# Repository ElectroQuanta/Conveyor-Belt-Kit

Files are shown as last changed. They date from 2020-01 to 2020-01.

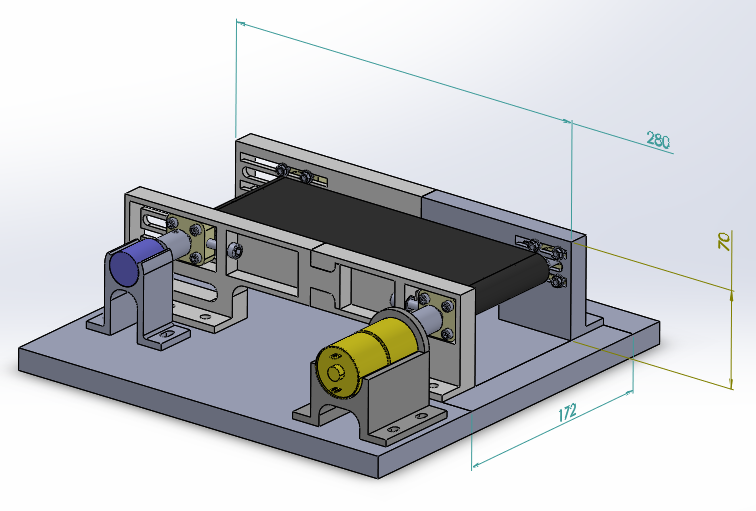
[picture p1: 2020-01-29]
Mechanics/mechanics.png

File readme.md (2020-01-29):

- [Introduction](#org74c4463)
  - [Motivation & Goals](#org79d08ed)
  - [Product concept](#orgb032d50)
- [Repository Struct](#org79cf582)

# Introduction

The present work, within the scope of the curricular unit of Laboratórios e Práticas Integradas I, consists in the project of the development of a product, namely, a pedagogic kit about automatic control. The theme selected by the project’s team was a conveyor belt, showcasing the velocity control of the load transported by the conveyor, independently from its mass. In this section are presented the project’s motivation and goals, the product concept, the project planning and the document organisation.

## Motivation & Goals

The main goal of the project is to develop a didactic kit to ease the learning of automatic control with the following characteristics:

-   Low complexity — to be an useful tool in a wide range of ages;
-   Subject comprehensive — to be able to integrate topics on several domains of electronics engineering, with particular focus on the curricular units taught on the fifth semester of the MIEEIC;
-   affordable: to allow replication and usage by any social stratum;
-   safe: without posing any danger for the user well-being and the surrounding ones, as well as not causing any materials.
-   didactic: fostering the learning on the topics in a practical and fun way;
-   pedagogic: documenting the project to allow replication by any individual in a simple and convenient manner.

## Product concept

The envisioned product consists of a didactic kit to enable the learning about automatic control. For this purpose, it focuses on a simple control problem — load movement control (velocity and direction) in a conveyor, similar to the ones present at the airports for user transportation. However, it will allow the user to experiment several types of controllers and the effect of each one in the system to control.

The goal is to control the velocity of the conveyor, virtually independently of its load. Thus, the addition or removal of load (e.g. passengers) should not affect the velocity of the conveyor. Additionally, the transportation direction must also be modifiable.

Furthermore, a laboratory guide is to be produced, similar to the ones used in Laboratórios e Práticas Integradas I (LPI1).

# Repository Struct

-   Control Guidebook: contains the guidebook created from the project
-   Datasheets: contains the relevant electronics datasheets
-   Manuals: contains the assembly manual and the user manual
-   Mechanics: contains the mechanics parts (STL format) for 3D printing:
-   PCB: printed circuit board - Bill of Materials, Schematics and Layouts
-   Simulations: control simulations
-   Tests: relevant tests performed

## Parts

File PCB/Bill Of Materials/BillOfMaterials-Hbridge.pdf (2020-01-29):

|Bill Of Materials for h-bridge_circuit.sch on Mon Jan 20 15:50:08 2020 | |
|Item|Qty |Reference|Part Name | |Manufacturer | |Description | |Value |
|----+----+---------+--------------+--------------+-----------------------------+------|
|1 | |1 | |C2 | |CAP-CK05,10n, |KEMET | |RADIAL CERAMIC CAPACITOR, | |10n | |
| | | | | | |??? | | | |MIL-SPEC SIZE CK05 | | | |
|2 | |1 | |C1 | |CAP-CK05,22n, |KEMET | |RADIAL CERAMIC CAPACITOR, | |22n | |
| | | | | | |??? | | | |MIL-SPEC SIZE CK05 | | | |
|3 | |1 | |C4 | |CAP-CX12-B,1u,|KEMET | |POL. DIPPED SOLID TANT. CAP. |1u | |
| | | | | | |??? | | | |MIL-SPEC SIZE CX12 CASE 'B' | | | |
|4 | |1 | |C3 | |CAP-CX12-B, | |KEMET | |POL. DIPPED SOLID TANT. CAP. |22u | |
| | | | | | |22u,??? | | | |MIL-SPEC SIZE CX12 CASE 'B' | | | |
|5 | |2 | |J1 J4 | |CONRA-2P-200 | | | |RIGHT ANGLE 2-PIN M/F | | | |
| | | | | | | | | | |HORIZONTAL PCB CONNECTOR | | | |
|6 | |1 | |J3 | |CONRA-3P-200 | | | |RIGHT ANGLE 3-PIN M/F | | | |
| | | | | | | | | | |HORIZONTAL PCB CONNECTOR | | | |
|7 | |4 | |D1-4 | |DIODE | | | |GENERIC DIODE W ALTERNATE | | | |
|8 | |1 | |F2 | |FUSE | | | | | | | |
|9 | |1 | |U1 | |L298N | | | |Dual_Full_Bridge_Motor_Driver| | |
| | | | | | | | | | |_15-Pin(15+Tab)_MULTIWATT_V_T| | |
| | | | | | | | | | |ube | | | |
|10 | |1 | |U2 | |MC7805ACT | |MOTOROLA | |POSITIVE VOLTAGE REGULATOR; | | | |
| | | | | | | | | | |FIXED +5.0 VOLTS | | | |
|11 | |4 | |H1-4 | |PCB_HOLE | | | | | | | |

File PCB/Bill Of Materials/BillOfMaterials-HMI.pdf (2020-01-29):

|Bill Of Materials for hmi_circuit.sch on Mon Jan 20 15:45:06 2020 | |
|Item|Qty |Reference|Part Name | |Manufacturer | |Description | |Value |
|----+----+---------+--------------+--------------+-----------------------------+------|
|1 | |1 | |C2 | |CAP-CK05,10n, |KEMET | |RADIAL CERAMIC CAPACITOR, | |10n | |
| | | | | | |??? | | | |MIL-SPEC SIZE CK05 | | | |
|2 | |1 | |C1 | |CAP-CK05,22n, |KEMET | |RADIAL CERAMIC CAPACITOR, | |22n | |
| | | | | | |??? | | | |MIL-SPEC SIZE CK05 | | | |
|3 | |1 | |J1 | |CONRA-2P-200 | | | |RIGHT ANGLE 2-PIN M/F | | | |
| | | | | | | | | | |HORIZONTAL PCB CONNECTOR | | | |
|4 | |1 | |J2 | |CONRA-4P-200 | | | |RIGHT ANGLE 4-PIN M/F | | | |
| | | | | | | | | | |HORIZONTAL PCB CONNECTOR | | | |
|5 | |1 | |LED_DRIVE|LM3914N | | | |<b>LED_DRIVER</b><p>_senses_a| | |
| | | | |R | | | | | |nalog_voltage_levels_and_driv| | |
| | | | | | | | | | |es_10_LEDs | | | |
|6 | |1 | |VREG | |MC7805ACT | |MOTOROLA | |POSITIVE VOLTAGE REGULATOR; | | | |
| | | | | | | | | | |FIXED +5.0 VOLTS | | | |
|7 | |10 | |L1-10 | |MLED71 | |MOTOROLA | |INFRARED LED | | | |
|8 | |4 | |HOLE1-4 | |PCB_HOLE | | | | | | | |
|9 | |3 | |R1 R3-4 | |RES-1/8W,10k | | | |RES BODY:060 CENTERS:400 | |10k | |
|10 | |1 | |R2 | |RES-1/8W,2.2k | | |RES BODY:060 CENTERS:400 | |2.2k | |
|11 | |1 | |SW2 | |SWITCH-SP,??? | | |SWITCH | |??? | |
|12 | |1 | |SW1 | |SWITCH-ST | | | |WIRE CONNECTION | | | |
|13 | |1 | |POTV | |VRES-TOP-ADJ | | | |VARIABLE RESISTOR (TOP ADJUST| | |
| | | | | | | | | | |TYPE) | | | |

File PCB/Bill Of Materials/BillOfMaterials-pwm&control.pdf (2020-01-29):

|Bill Of Materials for Pwm_Control_V4.sch on Fri Jan 24 15:55:29 2020 | |
|Item|Qty |Reference|Part Name | |Manufacturer | |Description | |Value |
|----+----+---------+--------------+--------------+-----------------------------+------|
|1 | |1 | |C3 | |CAP-CK05,10n, |KEMET | |RADIAL CERAMIC CAPACITOR, | |10n | |
| | | | | | |??? | | | |MIL-SPEC SIZE CK05 | | | |
|2 | |1 | |C2 | |CAP-CK05,22n, |KEMET | |RADIAL CERAMIC CAPACITOR, | |22n | |
| | | | | | |??? | | | |MIL-SPEC SIZE CK05 | | | |
|3 | |1 | |C1 | |CAP-CK05,330n,|KEMET | |RADIAL CERAMIC CAPACITOR, | |330n | |
| | | | | | |??? | | | |MIL-SPEC SIZE CK05 | | | |
|4 | |1 | |C5 | |CAP-CK05,???, |KEMET | |RADIAL CERAMIC CAPACITOR, | |??? | |
| | | | | | |??? | | | |MIL-SPEC SIZE CK05 | | | |
|5 | |1 | |C4 | |CAP-CX12-B, | |KEMET | |POL. DIPPED SOLID TANT. CAP. |??? | |
| | | | | | |???,1u | | | |MIL-SPEC SIZE CX12 CASE 'B' | | | |
|6 | |1 | |J2 | |CONRA-2P-200 | | | |RIGHT ANGLE 2-PIN M/F | | | |
| | | | | | | | | | |HORIZONTAL PCB CONNECTOR | | | |
|7 | |1 | |J1 | |CONRA-5P-200 | | | |RIGHT ANGLE 5-PIN M/F | | | |
| | | | | | | | | | |HORIZONTAL PCB CONNECTOR | | | |
|8 | |2 | |D1-2 | |DIODE | | | |GENERIC DIODE W ALTERNATE | | | |
|9 | |1 | |U1 | |LM324 | |MOTOROLA | |QUAD DIFFERENTIAL INPUT | | | |
| | | | | | | | | | |OPERATIONAL AMPLIFIER | | | |
|10 | |1 | |U2 | |MC7805ACT | |MOTOROLA | |POSITIVE VOLTAGE REGULATOR; | | | |
| | | | | | | | | | |FIXED +5.0 VOLTS | | | |
|11 | |1 | |D6 | |MLED71 | |MOTOROLA | |INFRARED LED | | | | |
|12 | |4 | |H1-4 | |PCB_HOLE | | | | | | | | |
|13 | |2 | |R1 R6 | |RES-1/4W,100k | | |RES BODY:100 | CENTERS:500 | |100k | |
|14 | |2 | |R2 R22 | |RES-1/4W,10k | | | |RES BODY:100 | CENTERS:500 | |10k | |
|15 | |1 | |R7 | |RES-1/4W,1k | | | |RES BODY:100 | CENTERS:500 | |1k | |
|16 | |1 | |R5 | |RES-1/4W,200 | | | |RES BODY:100 | CENTERS:500 | |200 | |
|17 | |1 | |R3 | |RES-1/4W,43k | | | |RES BODY:100 | CENTERS:500 | |43k | |
|18 | |1 | |R8 | |RES-1/4W,51k | | | |RES BODY:100 | CENTERS:500 | |51k | |
|19 | |15 | |R9-21 | |RES-1/4W,??? | | | |RES BODY:100 | CENTERS:500 | |??? | |
| | | | |R23-24 | | | | | | | | | | |
|20 | |2 | |U3-4 | |TL084CN | | | |JFET_quad_operational_amplifi| | |
| | | | | | | | | | |ers | | | | |
|21 | |1 | |R4 | |VRES-TOP-ADJ | | | |VARIABLE RESISTOR (TOP ADJUST| | |
| | | | | | | | | | |TYPE) | | | | |

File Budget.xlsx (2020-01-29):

Description | Value (€) | Supplier | Category
Electronic box & Connectors | 15.98 | Leroy Merlin | Casing & Connectors
Electronic box connectors & Power supply connectors | 4.4 | Botnroll | Casing & Connectors
Power supply case | 3.69 | Botnroll | Casing & Connectors
Mechanical Components | 14 | ELAX | Mechanical
Mechanical 3D printed components | 20 | NEEEICUM | Mechanics
Control PCB components | 4.92 | Botnroll | PCB
Actuator PCB | 6 | Oficinas DEI | PCB
Actuator PCB components | 10.55 | Botnroll | PCB
Control PCB | 11 | Oficinas DEI | PCB
HMI PCB | 6 | Oficinas DEI | PCB
Total | 96.54

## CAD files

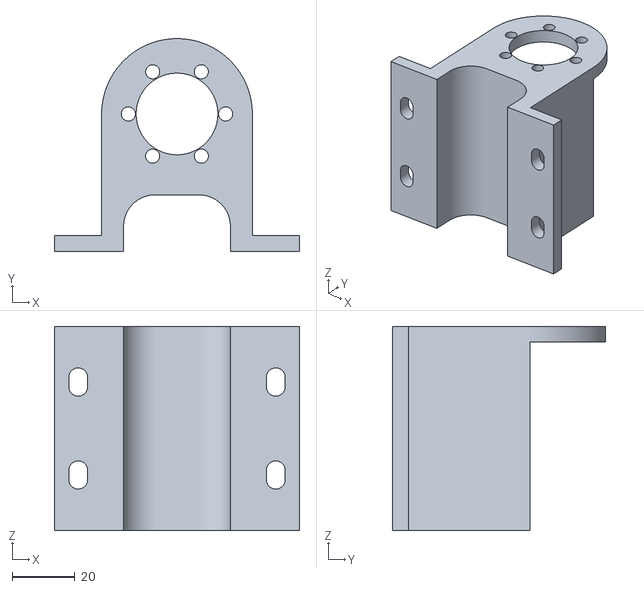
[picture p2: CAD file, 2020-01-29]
Mechanics/STL/Suporte_Motor.STL
78.0 x 67.8 x 65.0

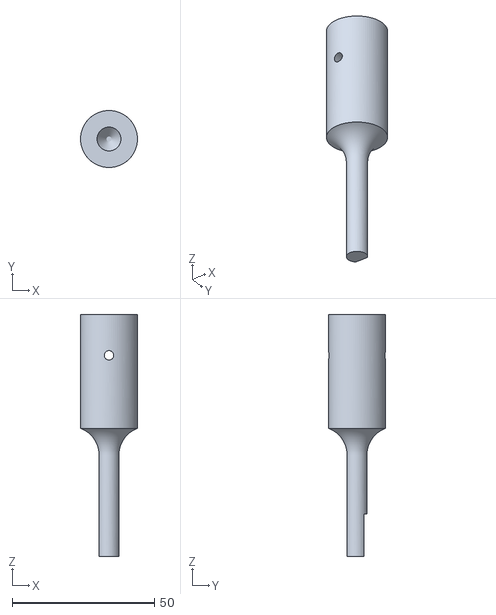
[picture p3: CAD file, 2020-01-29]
Mechanics/STL/Veio_2B_new_version.STL
20.0 x 20.0 x 85.0

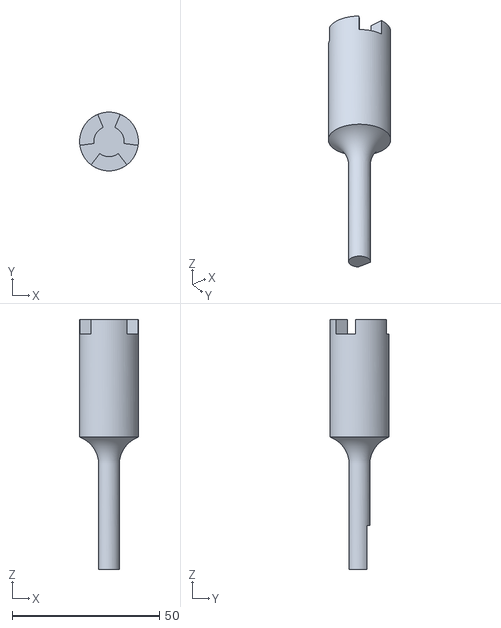
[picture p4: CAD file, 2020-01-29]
Mechanics/STL/Veio_1B.STL
20.0 x 20.0 x 85.0

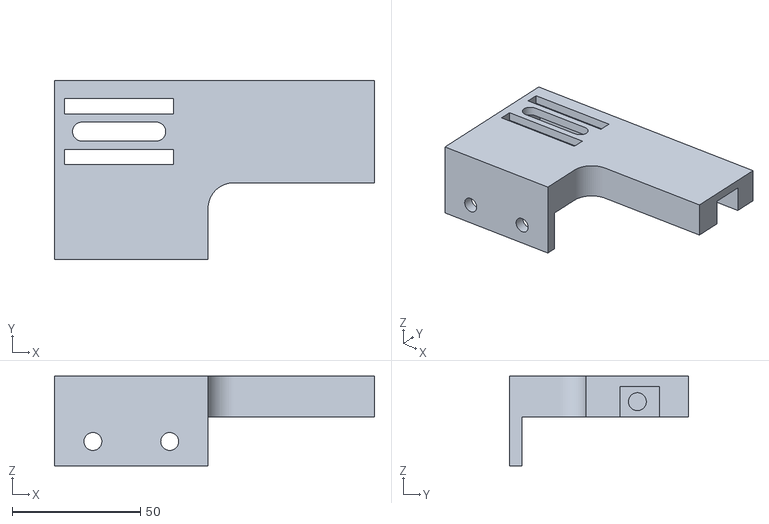
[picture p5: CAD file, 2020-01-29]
Mechanics/STL/Estrutura_1B.STL
125.0 x 70.0 x 35.0

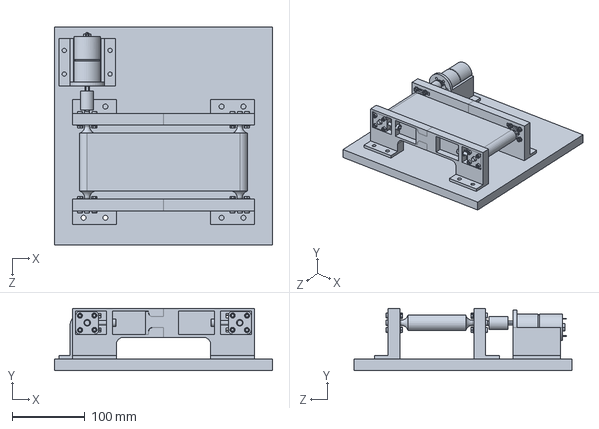
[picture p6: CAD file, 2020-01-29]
Mechanics/STL/Veio_1A_x2.SLDPRT
300.0 x 86.0 x 300.0 mm

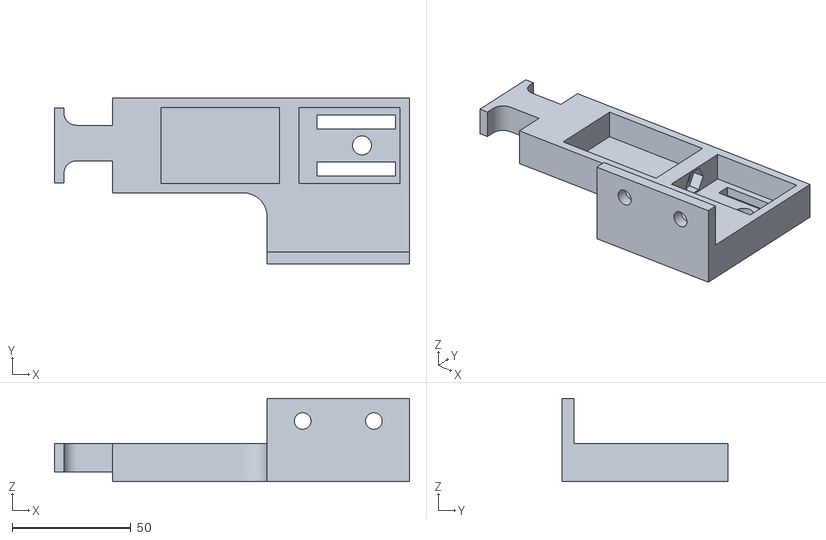
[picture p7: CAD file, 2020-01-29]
Mechanics/STL/Apoio_estutura_2.STL
149.5 x 70.0 x 35.0

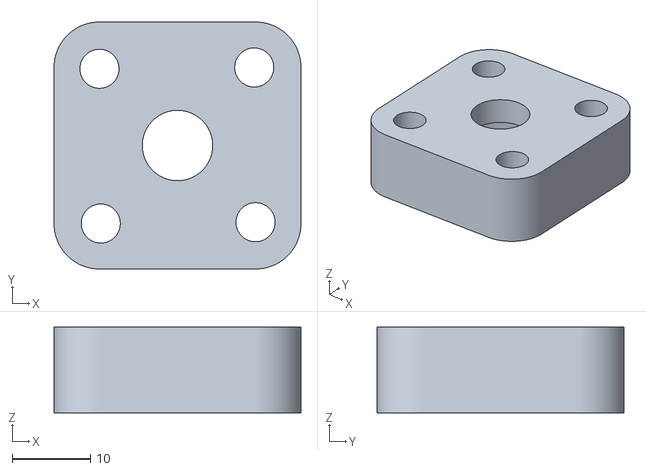
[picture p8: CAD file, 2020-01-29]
Mechanics/STL/Tensionador_x4.STL
31.6 x 31.6 x 11.0

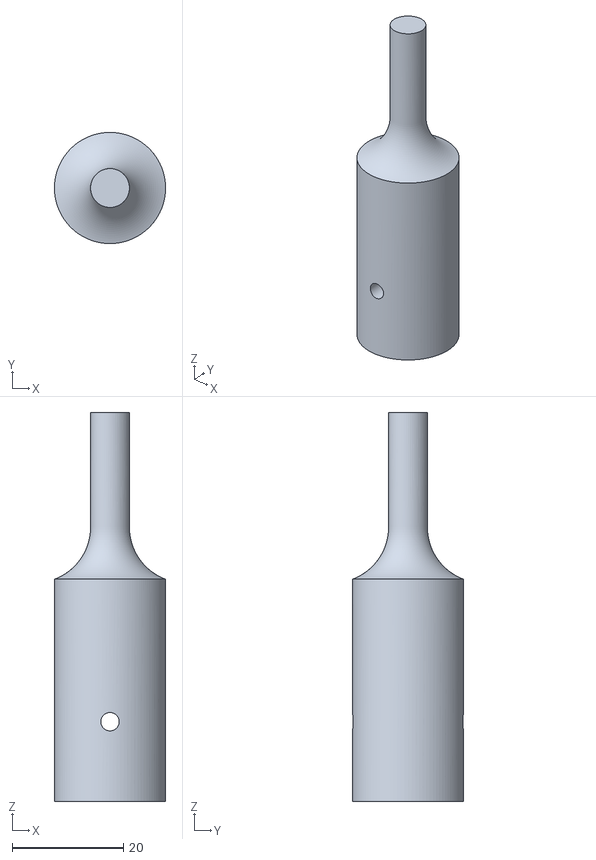
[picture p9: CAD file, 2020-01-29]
Mechanics/STL/Veio_2A_new_version.STL
20.0 x 20.0 x 70.0

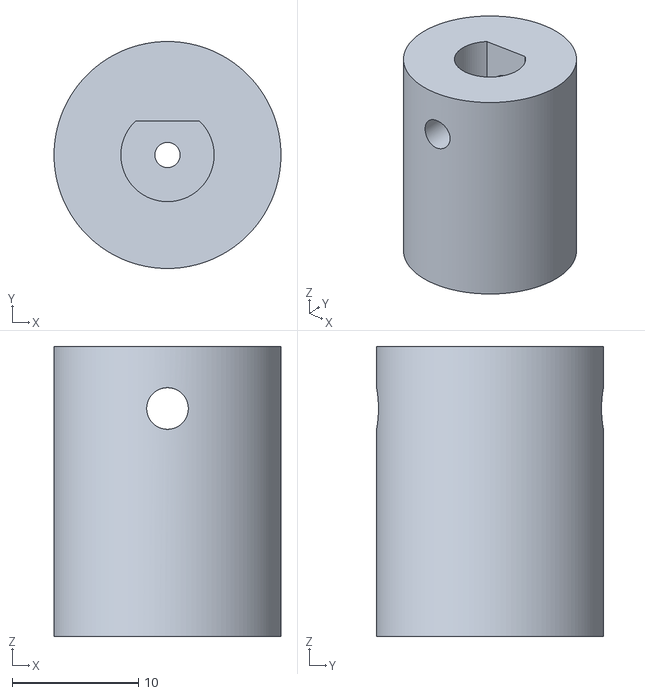
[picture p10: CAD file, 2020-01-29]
Mechanics/STL/Acoplamento_motor_feedBack.STL
18.0 x 18.0 x 23.0

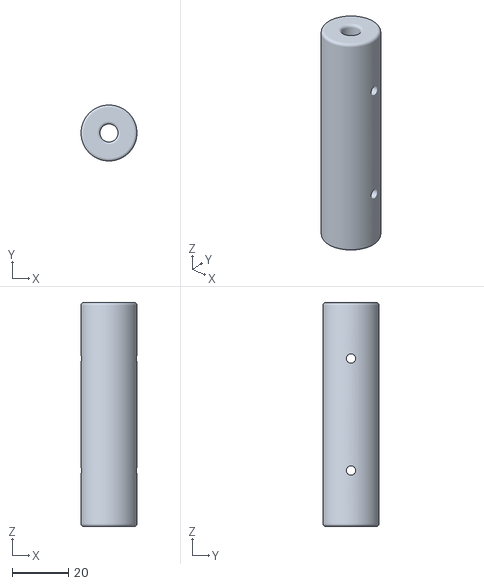
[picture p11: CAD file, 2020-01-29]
Mechanics/STL/Cilindro_veio_6mm.STL
20.0 x 20.0 x 80.0

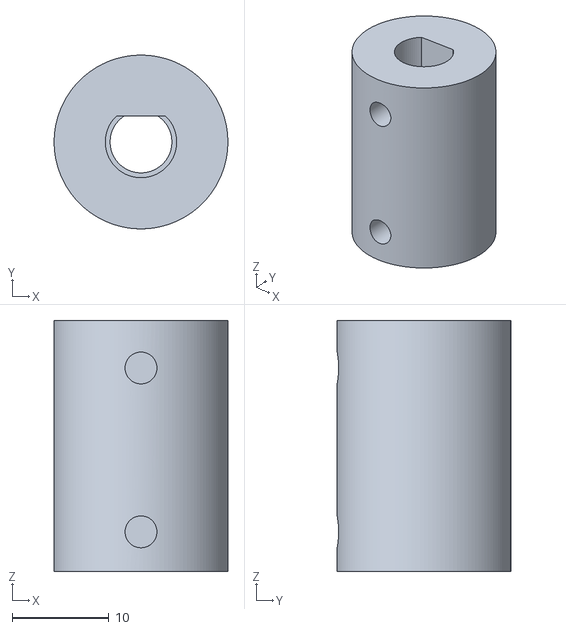
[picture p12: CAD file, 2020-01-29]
Mechanics/STL/Acoplamento.STL
18.0 x 18.0 x 26.0

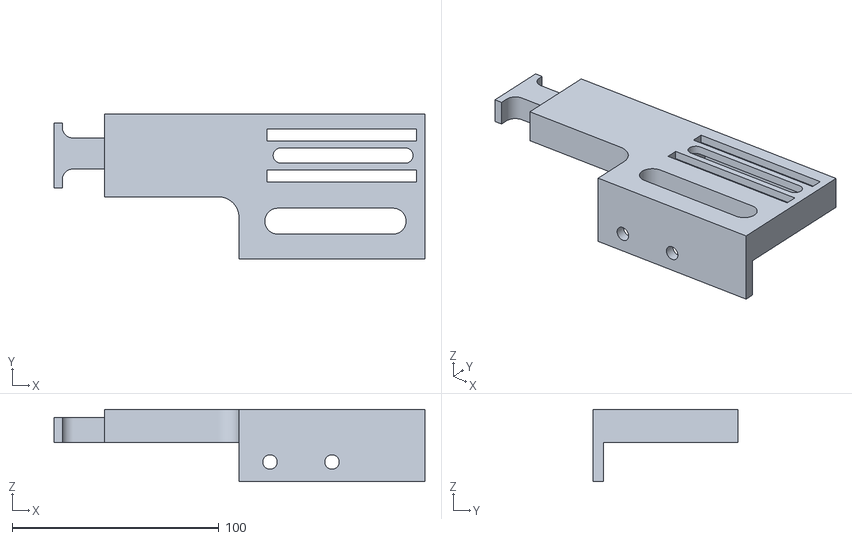
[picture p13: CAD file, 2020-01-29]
Mechanics/STL/Estrutura_2B.STL
179.5 x 70.0 x 35.0

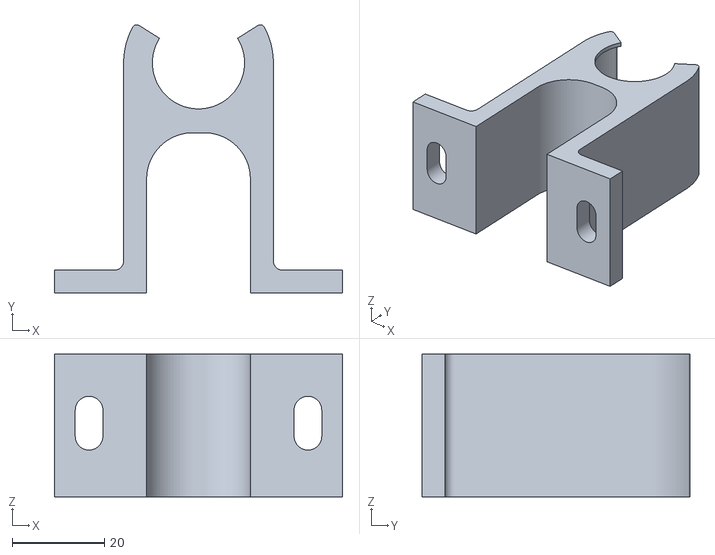
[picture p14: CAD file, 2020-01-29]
Mechanics/STL/Suporte_Motor_feedBack.STL
62.5 x 58.3 x 31.0

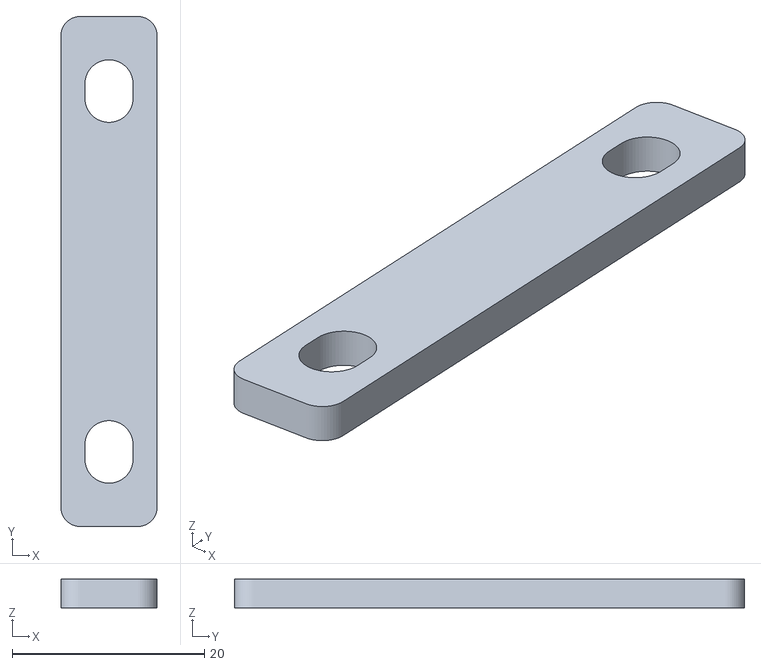
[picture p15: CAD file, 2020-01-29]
Mechanics/STL/Suporte_placa.STL
10.0 x 53.0 x 3.00

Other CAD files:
Mechanics/STL/Veio_2B.STL
Mechanics/STL/Apoio_estutura_1.STL
Mechanics/STL/Estrutura.STL
Mechanics/STL/Apoio_veio.STL
Mechanics/STL/Estrutura_1A.STL
Mechanics/STL/Estrutura_2A.STL
Mechanics/STL/Veio_1A_x2.STL
Mechanics/STL/Veio_1B_new_version.STL

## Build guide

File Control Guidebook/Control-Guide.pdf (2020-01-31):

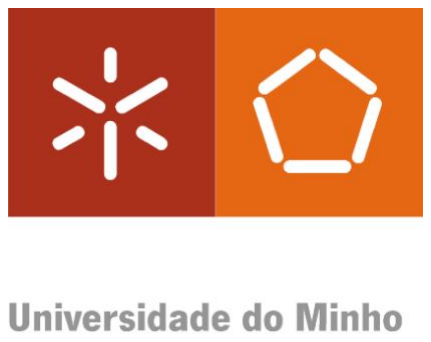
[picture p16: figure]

## Laboratório e Práticas Integradas I 2019/20 Integrator Project

## Integrated Master´s in Engineering

## Industrial Electronics and Computers

# Conveyor Belt velocity control: laboratory guide

Group 3:

José Pires | A50178
Hugo Carvalho | A85156
Nuno Rodrigues | A85207
João Faria | A85632
João Carvalho | A83564
Hugo Ferreira | A80665

30th January of 2020

## 1.Introduction

This laboratory practice focuses on the control of the velocity of a conveyor belt considering all types of control on the curriculum of the UC Automatic Control + Proportional-Integral.

Specifically, an electronic system will control a laboratorial model of a conveyor belt, which allows the simulation of all characteristics of the merchandised version, represented Figure 1.

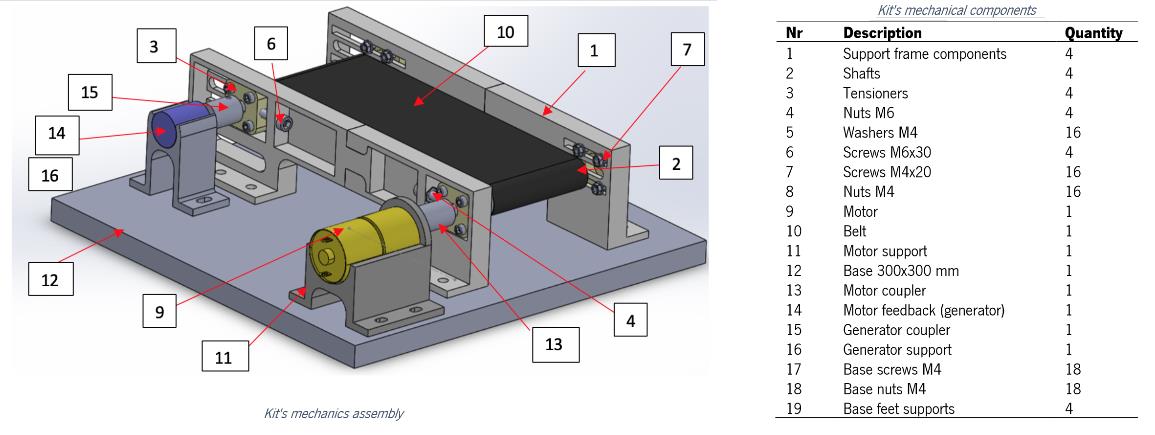
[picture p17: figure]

Figure 1- Laboratorial Model of Conveyor Belt

The motor is fed a voltage causing it to start rotating. The generator, acting as a sensor, will then apply a voltage to its terminals, based on the conveyor belt’s speed, thus providing a feedback path for the control.

The control system will require a sensor, a controller and an actuator.
As mentioned before, in this model of the conveyor belt, the generator will act as the sensor, supplying a “variable to control”.

The controller has several duties:

- Establishing a reference variable, or more accurately, an electrical representation of it.
- Establishing the electrical representation of the error.
- Establishing a command voltage, using the reference and measured variables previously

mentioned and a control rule.

In this model, there will be several controllers, each employing a different control rule, present in this document on Figure 3 and Figure 6.

The actuator serves as the connector between motor and controller, it will apply the command variable on the motor, permitting that the controller’s changes to the system be shown.

The control rules to be applied can be succinctly described as follows:

- On-Off Control – It applies the maximum value of the command variable or the minimum

(in this case 0). In this specific case, the motor will either be rotating at full speed or not

rotating at all.

- Proportional Control – It applies a command variable between its maximum and minimum

value, proportional to the error.

- Proportional-Integral Control – Serves the same purpose as proportional control, control-

wise, but allows for better system performance, specifically by reducing the steady-state’s

error.

Due to the motor’s characteristics the actuator needs to be an H-bridge, represented by Figure 5.

All control rules require simulation, to implement a control rule without a clear idea of its consequences to the system, can be disastrous both for the model as well for a future career in engineering. In order to simulate, the system’s mathematical model and physical constant values must be obtained.

In all that follows consider +Vcc=12V and -Vcc=-12V. The opamps to be used are LM304 or equivalents.

## 2. Mathematical model

This prototype uses a DC motor and a reduction box with a reduction ratio of G:1 to move a cylinder that will in turn move the conveyor. Another DC motor, working as a generator is at the end of the conveyor, the latter moves a cylinder that will in turn move the generator.

Definitions:

J1: Motorized Cylinder’s Moment of Inertia

J2: Generator Cylinder’s Moment of Inertia

M: Conveyor’s Mass

w: Cylinder’s Angular Velocity

B: System’s Supposedly Linear Coefficient of Friction

The conveyor’s velocity (Control Variable) will be obtained by v = w * r, r being the cylinder’s radius. With this equality in mind we can obtain the system’s Lagrangian function:

L =

1
2

(J1 + J2 + Mr

2

)w²

With the Lagrangian, the system’s equation based on the torque is obtainable:

(J1 + J2 + Mr

2)

dw
dt = T − Bw (2)

Considering that the motor is of the DC variant and using the following definitions:

Ka: Motor’s Electromechanical Constant

I: Motor’s Current

Ua: Motor’s Voltage

R: Rotor’s Resistance

wm: Motor’s Angular Velocity

This relation is obtained:
T = G ∗ Ka ∗ I

I =

1
R

(Ua − Ka ∗ wm)

Considering that:

wm = G ∗ w

The expression above can be simplified further: T = Km ∗ I,Km = Ka ∗ G

I =

1
R

Ua −

Km
R

w

In conclusion, the following model is obtained:

(J1 + J2 + Mr

2
)

dw
dt + (B +

(Km)

2
R

)w =

Km
R

Ua

A first-degree model with one control variable resulting in a single feedback gain.

## 2.1 – Obtain the physical constants of the system

Before drafting any kind of control diagram, the system’s physical constants are required for an accurate simulation. Following the mathematical module, the following constants are required:

- M – Conveyor’s mass
- m – Cylinder’s mass
- r – Radius of the cylinder’s base
- J1 – Moment of inertia of the motor’s cylinder
- J2 – Moment of inertia of the generator’s cylinder
- B – Supposedly linear coefficient of friction
- Km – Motor’s electromechanical constant (with reduction box)
- R – Rotor’s resistance

2.1.1- Measure M, m and r with appropriate measuring instruments and calculate J1 and J2 with those values.

2.1.2 – Run a series of tests to obtain physical constants.

Consider the following equations:

Km =

T
I

B =

T
w

Un = R ∗ ia + Ka ∗ w
≡ R = Un/Ia + 0, w = 0

T − Torque obtained when the motor is rotating at a constant angular velocity. I – Nominal current.
w – The constant angular velocity of the motor.
Un – Nominal voltage of the motor.
Ia – Start-up current of the motor.

2.1.2.1- Build a simple circuit with a DC power source (+Vcc) in series with a 1-ohm resistor and the motor. Measure, with an amperemeter, the current that passes through the motor when it rotates with constant velocity. Calculate the motor’s potency.

2.1.2.2- With the motor’s potency, calculate the torque and with it Km and B.

2.1.2.3- With the same circuit as in 1.2.1, using an oscilloscope measure the motor’s startupcurrent and calculate R.

## 3 – On-Off Control Simulation

Before implementing any electronic circuit with the purpose of controlling a system, the method
of control | must | be | chosen | and | its | suitability | towards | the | system | analyzed.
Following the Automatic Control UC’s curriculum, on-off control will be considered first:

3.1- Using the provided mathematical module and system’s physical constants develop a simulation draft implementing on-off control.

3.2- Draw conclusions considering the physical consequences of the system’s behavior with on-off control. Can it be implemented? Should it be implemented? Justify your answers adequately.

## 4- Proportional Control Simulation

Once again before considering implementing a circuit, the control rule’s compatibility towards the system must be tested through simulation.

4.1- Develop a simulation draft using proportional control. Obtain an appropriate gain, that is physically possible to use for proportional control.

4.2- Draw conclusions. Does the system do what its supposed to? Does it reach the level of control desired? Why?

4.3- Compare to the results of the on-off simulation. Is it better? Why?

## 5-Measure the voltage of generator

As the belt moves, a voltage in the terminals of the generator appears in the mV range. This voltage is crucial to control the velocity of the belt, it is the feedback signal that informs the controller of the value of the velocity of the belt. This value will be compared to the reference voltage, which varies between 0 and 5V so the voltage of the generator needs to be betwixt 0 and 5 V as well.

To do so, the first thing is to make a motor and generator test, where one varies the voltage in the motor and reads the voltage in the terminals of the generator. Inputting the values in an excel sheet and drawing the tendency line, the result must be an almost linear slope. This slope defines the gain necessary to use in a non-inverting opamp montage.

Furthermore, the generator voltage must pass throw a low pass filter for the ripple oscillations to disappear.

After the non-inverting opamp montage, it must pass through a full-wave rectifier (R4=R5). Should the motor be rotating counter-clockwise, the voltage at the generator’s terminals will be negative, which must not happen for our actuator is an H-Bridge.

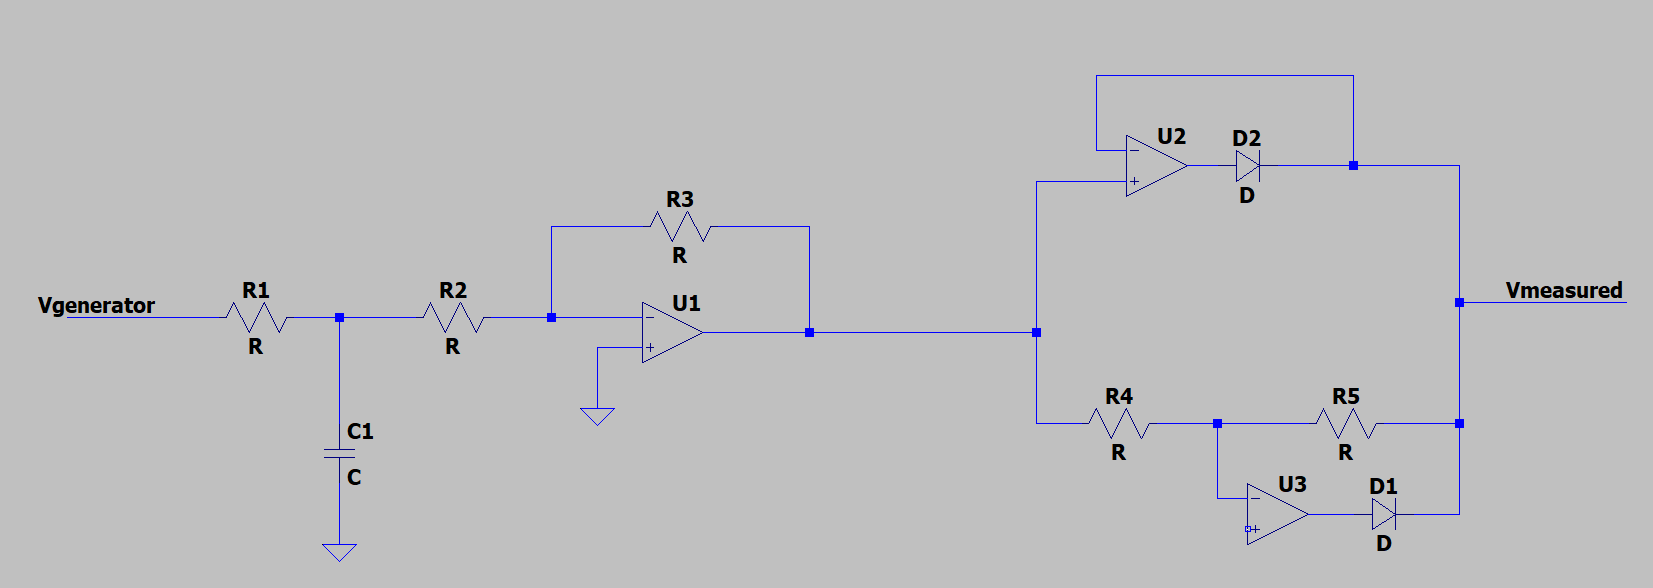
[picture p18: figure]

Figure 2 – Vmeasured Circuit

5.1 – Make the motor/generator test and draw the tendency line in excel.

5.2- Dimension R1 and C1 for the cutoff frequency to be 1 Hz.

5.3- Dimension R2 and R3 for Vmeasured to vary between 0 and 5V

## 6-Proportional Control Circuit

The implementation of proportional control can be obtained by the circuit in Figure 3.

The circuit using +Vstat, the RV1 potentiometer and 100-ohm resistor serves allows the generation of a Vreference voltage, the electrical representation of the conveyor’s desired velocity. The A2 opamp with the R3 and R4 resistors implement a subtractor resulting in:

Vcommand =

R3
R4

(Vreference − Vmeasured)

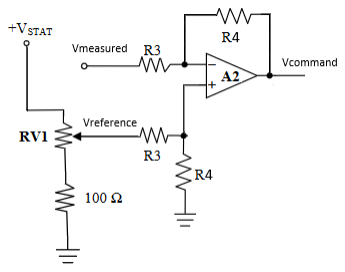
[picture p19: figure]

Figure 3- Circuit Implementing Proportional Control Rule

6.1-Study the behaviour of the circuit in Figure 3.

6.2- Calculate adequate values for R3 and R4 in order to obtain the gain that was deemed adequate in the simulation.

6.3- Assemble the circuit and test its behaviour. Make sure the opamp is behaving correctly.

## 6A-PWM based actuator

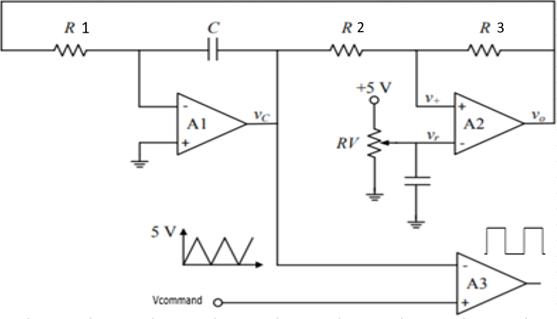
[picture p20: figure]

Figure 4- PWM signal generated by PWM modulator

Amplifier A1 is used in an inverter integrating assembly. Amplifier A2 is used in a non-inverting comparator assembly with hysteresis. Together, they generate a triangular wave between 0 and 5 V. The A3 amplifier performs a simple comparator, generating the PWM wave whose duty cycle is modified as the command tension varies.

The output wave, is high when the command voltage is higher than the triangular wave produced in the feedback loop, see Figure 4. Otherwise, it stays at 0V.

The PWM wave generated in the A3 interchanges between two values: 0V and 5V. However, when the duty cycle is changed (the time when it is 5V is changing) the medium voltage modifies, which is the product of the duty-cycle times high voltage (5V). That can be done, modifying the command voltage.

6.1A- Calculate the value of the components in the triangular wave:

a) Obtain the Vc expression in function of R1, C and Vo.
b) Determine R1 and C such that Vc takes 20ms from 0V to 5V.
c) Determine R2, R3 and Vr so that the comparator changes between 0V and 5V when Vo is +Vsat or -Vsat. Measure +Vsat and -Vsat.

6.2A- Draw Vo and Vc from 0ms to 40 ms.

6.3A- Draw Vcommand graph in function of Duty-cycle.

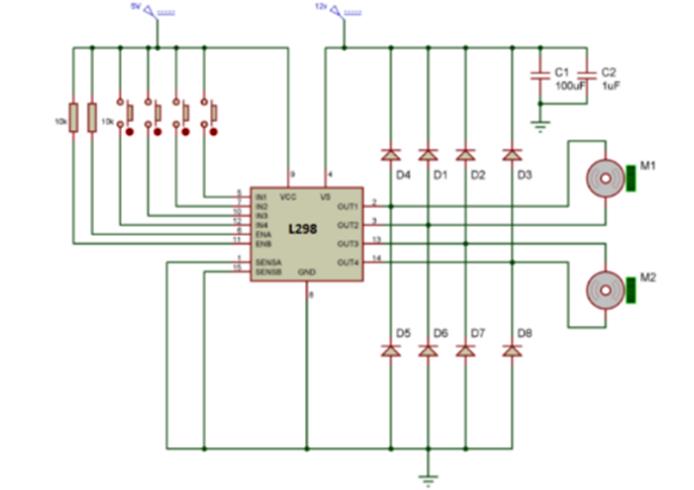
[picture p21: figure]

Figure 5- Actuator Circuit with the actuator part

6.4A- Which terminal should the A3 output be connected to? Assemble the following circuit, above in Erro! A origem da referência não foi encontrada.. Hint: The Enable terminal enables L298 internal H-Bridge.

a) Does the motor spin? Since only one motor will be used, which components are not useful for controlling motor M1?
b) Try pressing different buttons and adjust Vcommand so that the motor spins half the nominal value. Measure OUT1 and OUT2 tension.
c) Make the motor tension/velocity test and draw the tendency line in excel.

6.5A- Join the actuator’s exit to the motor’s terminals and observe the results. Does the system achieve the desired control?

## 7-PI Control

PI control is needed for non-integrating processes, in other words, any process that returns the same output given the same set of inputs and disturbances, one such example is a system whose control is not capable of reaching the desired level of control, normally due to physical limitations, more specifically once a certain point in the system’s response is reached, no matter how much the input or disturbance is changed (within physical reason of course) the system’s response will not change. In other words, a constant steady-state error is present!

The integrator will calculate the integer of the error and add it to Vcommand, therefore slowly reducing the steady-state error. The higher the integral gain, the faster the system’s steady-state error will decrease.

Vcommand = Kp ∗ Error + Ki ∗ ∫ Error

Integrator Output = −

1
R11 ∗ C

∫ Error

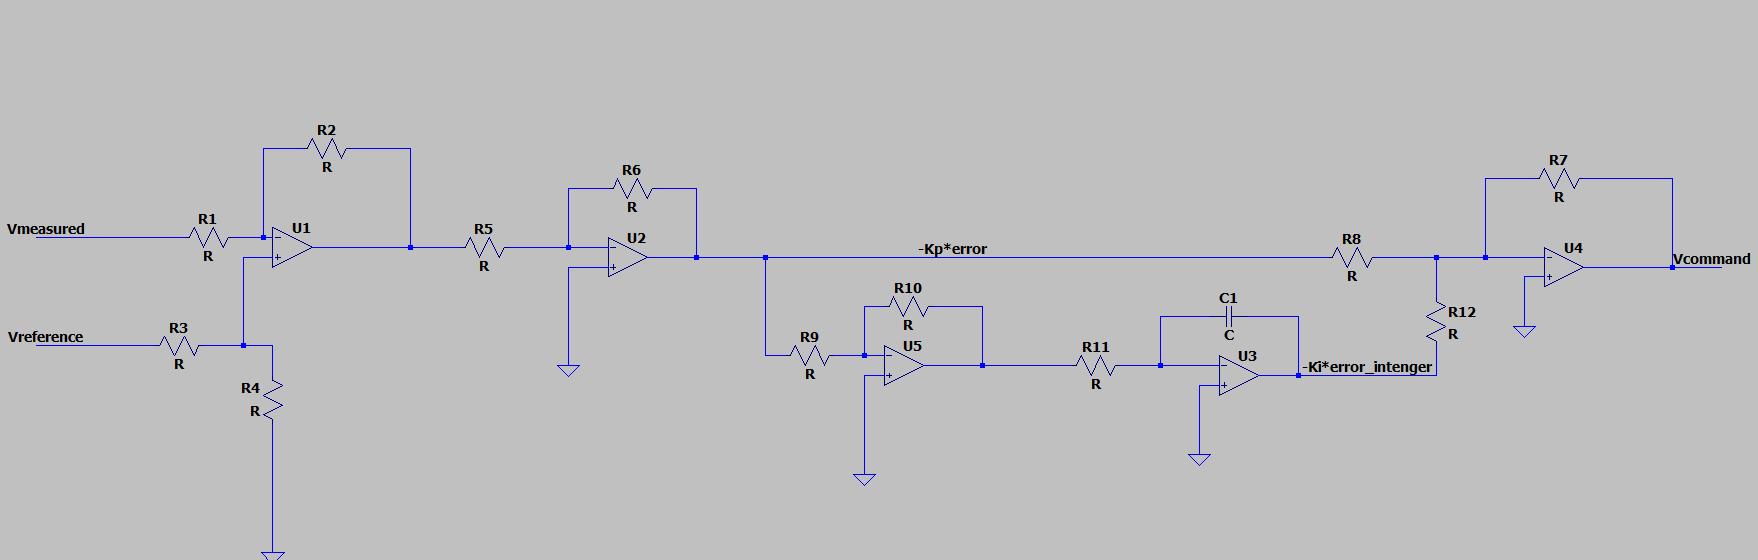
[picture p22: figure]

Figure 6- Circuit Implementing PI Control rule, R5=R6=R9=R10=R8=R7=R12=R7

7.1- Using the simulation diagram for 3.1, add integral control and comment on the result. Obtain a value for the integrator’s gain.

7.2- Study the circuit in Figure 6. What is the purpose of amplifiers U2, U3 and U5?

7.3- Use the PWM actuator to test the PI control on the motor. Measure the conveyor’s velocity and see if it reaches the value its supposed to. Compare to the results of the proportional gain.

7.4- Could PID control be used for this model? Why/Why not? What would be the consequences of forcing a derivative control?

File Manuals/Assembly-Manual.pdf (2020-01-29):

### A.3. Assembly manual

### A.3.1. Mechanics

Overview

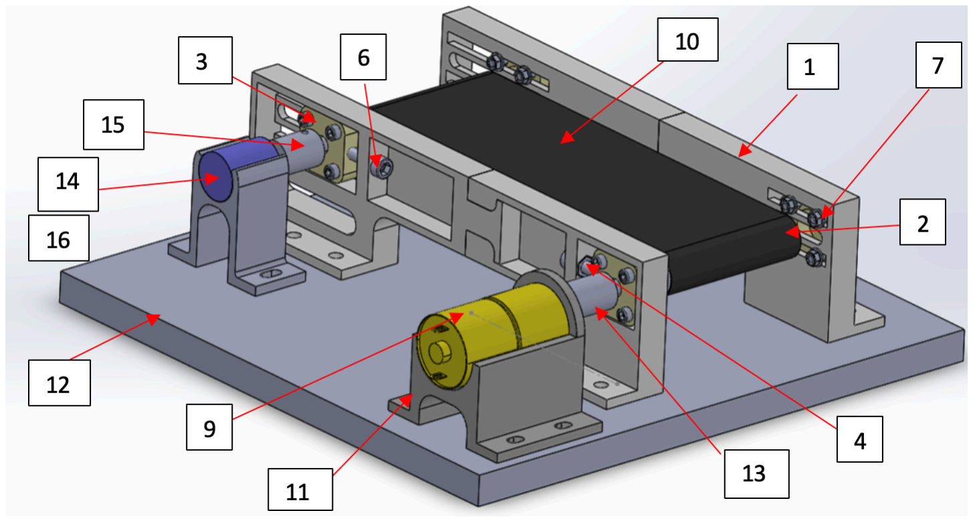
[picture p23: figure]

Figure Error! No text of specified style in document..1 - Kit's mechanics assembly

Table Error! No text of specified style in document..1 - Kit's mechanical components
Nr | Description | Quantity
1 | Support frame components | 4
2 | Shafts | 4
3 | Tensioners | 4
4 | Nuts M6 | 4
5 | Washers M4 | 16
6 | Screws M6x30 | 4
7 | Screws M4x20 | 16
8 | Nuts M4 | 16
9 | Motor | 1
10 | Belt | 1
11 | Motor support | 1
12 | Base 300x300 mm | 1
13 | Motor coupler | 1
14 | Motor feedback (generator) | 1
15 | Generator coupler | 1
16 | Generator support | 1
17 | Base screws M4 | 18
18 | Base nuts M4 | 18
19 | Base feet supports | 4

Follow these basic steps to assemble the kit’s mechanics:

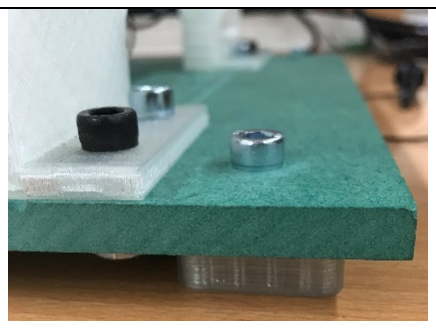
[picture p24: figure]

Step 1: screw the base’s
support using M6 bolts and
nuts;

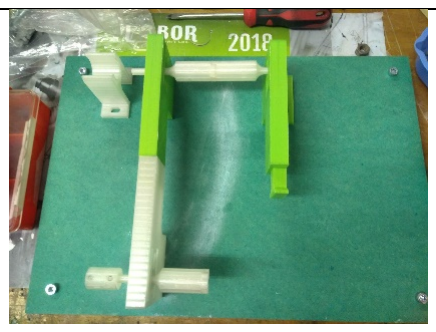
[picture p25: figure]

Step 2: Attach the support frame elements;

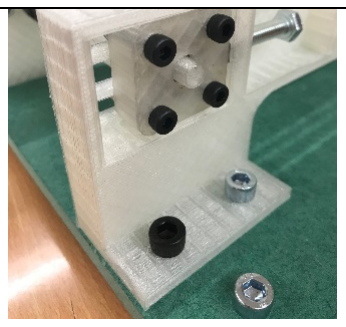
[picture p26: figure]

Step 3: Screw only one of the support frame elements to the base using M6 bolts and nuts;

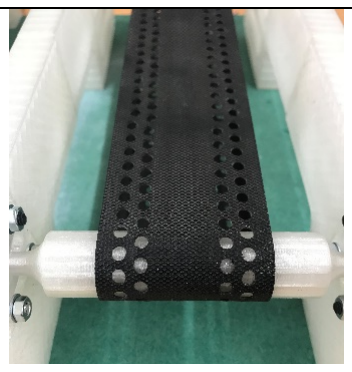
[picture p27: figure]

Step 4: Attach one of the
sides of shaft couples to the support frame already
screwed and insert the flat belt;

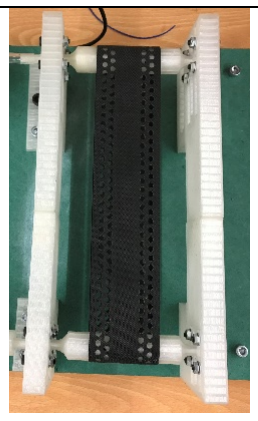
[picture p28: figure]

Step 5: Attach the other side of the shaft coupler to the opposite support frame and screw it to base using M6
bolts and nuts;

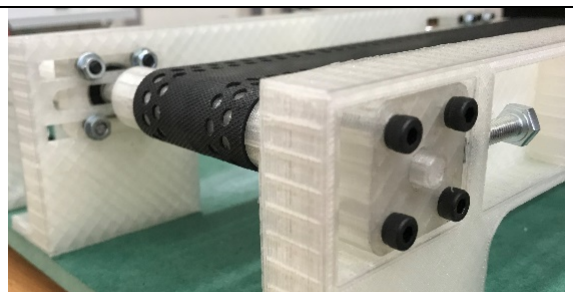
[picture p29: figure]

Step 6: Attach the tensioner to the shaft coupler and then screw it to the support frame using M4 bolts and nuts;

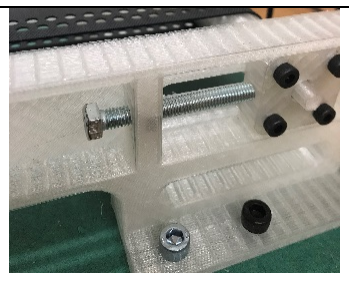
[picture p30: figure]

Step 7: Use the tensioner in order to regulate the tension of the flat belt;

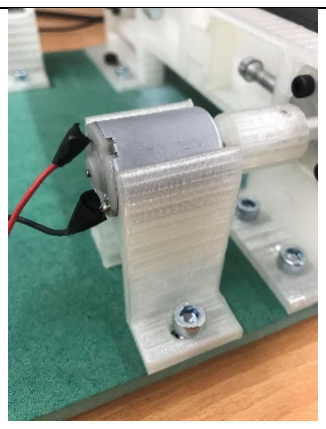
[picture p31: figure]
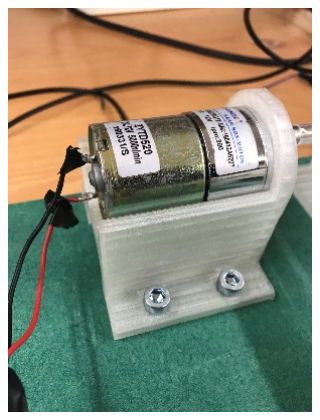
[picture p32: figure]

Step 8: Screw motor and
generator’s supports, then place them in the respective supports using M6 bolts and nuts;

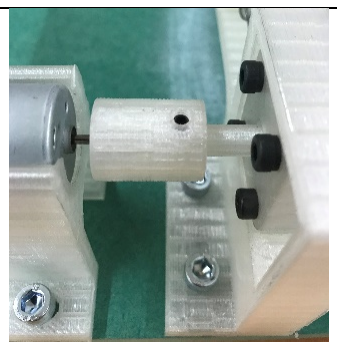
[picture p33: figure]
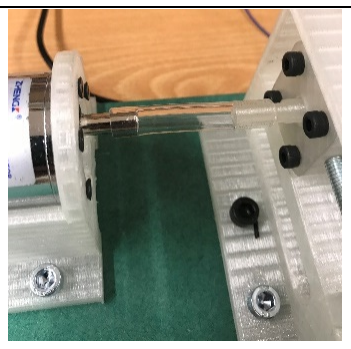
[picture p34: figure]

Step 9: Connect the driver and idler’s roller to the shaft coupler using the flexible joint;

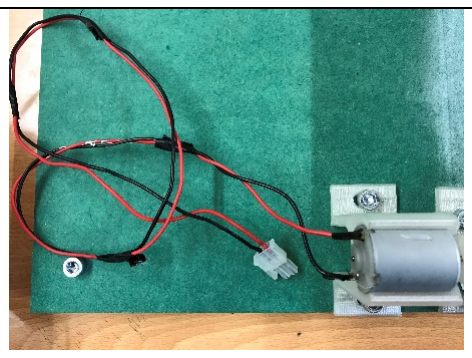
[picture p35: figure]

Step 10: Solder the Molex
connectors to the motor and the generator;

### A.3.2. Electronics

Follow these basic steps to assemble the kit’s electronics:

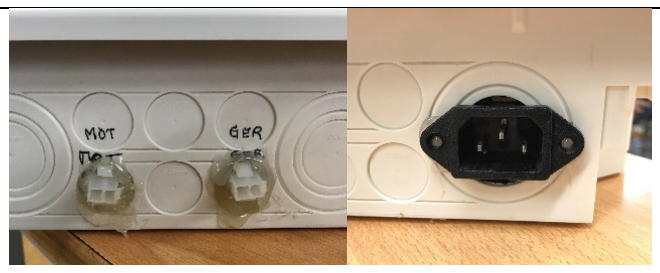
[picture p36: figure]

Step 0: Check if the electronic
box comes with the female
connectors for power supply and
motor and generator;

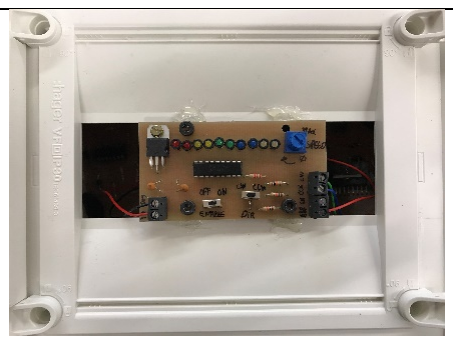
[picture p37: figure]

Step 1: screw the HMI’s PCB using M4 bolts and nuts and connect wires to the board connectors;

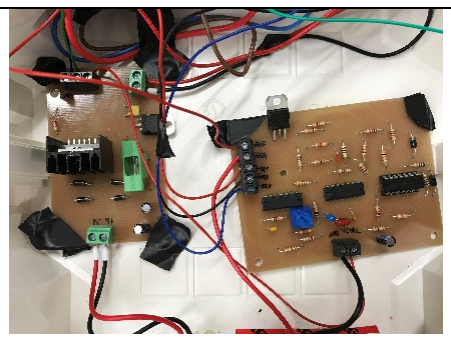
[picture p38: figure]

Step 2: Add wires to the Actuator and Controller PCBs and fixate them at the base of the electronic box;

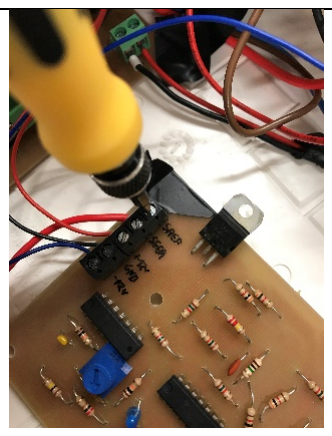
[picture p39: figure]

Step 3: Connect all wires to the appropriate places;

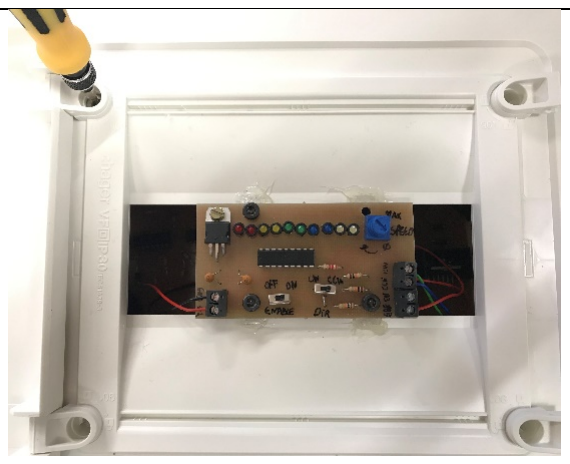
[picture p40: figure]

Step 4: Screw the electronic box cover with provided screws;

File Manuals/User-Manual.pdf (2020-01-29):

### A.4. User Manual

In this section, the user manual steps for connecting and operating the conveyor belt kit are briefly discussed.

The kit comes with the following components:

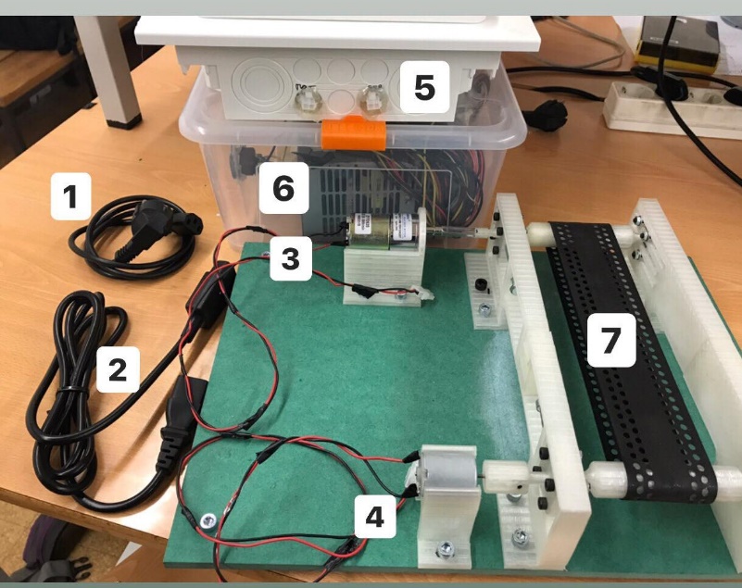
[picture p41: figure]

1) Power Supply cable;
2) Electronic box cable;
3) Motor wires;
4) Generator wires;
5) Electronic box;
6) Power Supply;
7) Conveyor belt;

The following steps are about how to turn on the system safely:

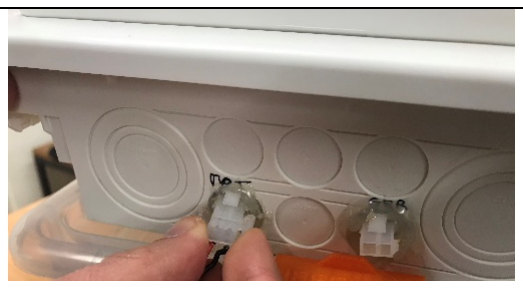
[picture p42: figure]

Step 1: Connect the motor wires (3)
to the electronic box (5);

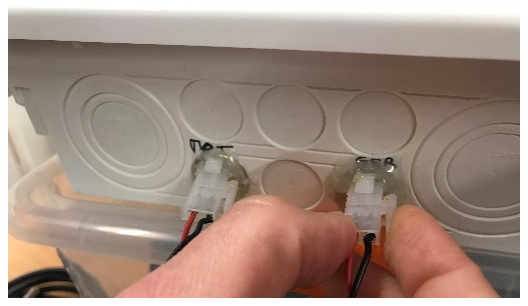
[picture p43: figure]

Step 2: Connect the generator wires
(4) to the electronic box (5);

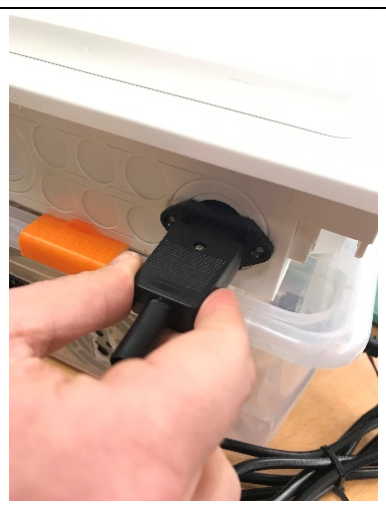
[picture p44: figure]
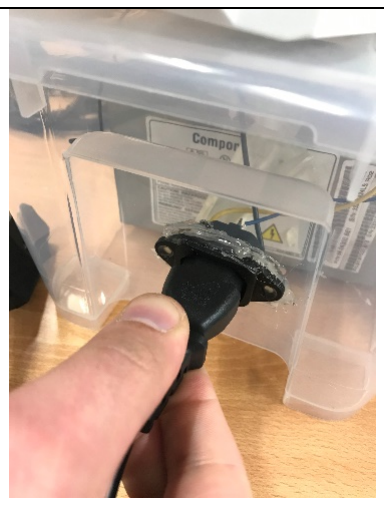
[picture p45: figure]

Step 3: By using the electronic box cable (2), connect the Power Supply
(6) to the Electronic Box (5);

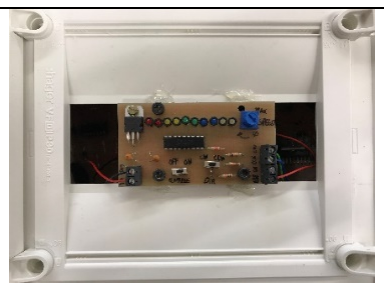
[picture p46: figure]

Step 4: Open the cover of the Electronic Box (5) and verify that Enable is OFF;

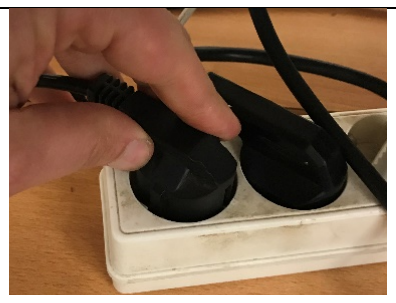
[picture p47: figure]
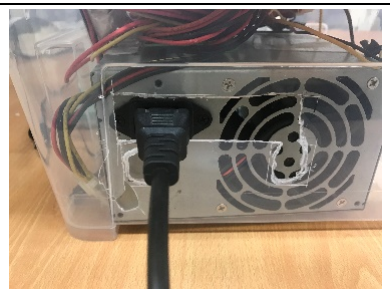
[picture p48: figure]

Step 5: Connect the power supply cable (1) to the Power supply (6) and then insert power supply cable in mains socket;
Step 6: Select Direction (Clockwise or Counter clockwise);
Step 7: Turn On Enable;

Step 8: Regulate blue knob to change speed; the leds should light up accordingly to the selected speed;

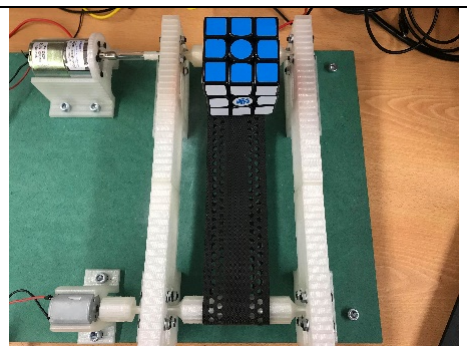
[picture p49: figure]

Step 9: Place the load at the beginning of the conveyor (7);
Step 10: To change direction, first turn the blue knob to minimum, then change direction and set the desire speed;

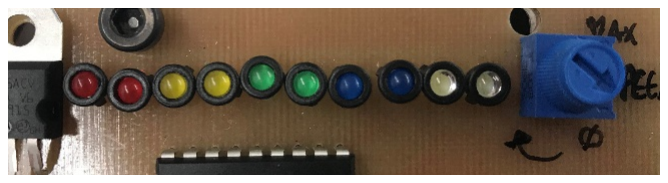
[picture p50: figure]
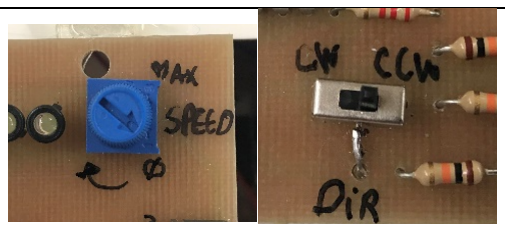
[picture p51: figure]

After using the product, the kit should be turned off correctly, accordingly to the following instructions:

- Step 1: Regulate the blue knob to the minimal speed;
- Step 2: Turn off Enable;
Step 3: Disconnect power supply cable (1) from socket;

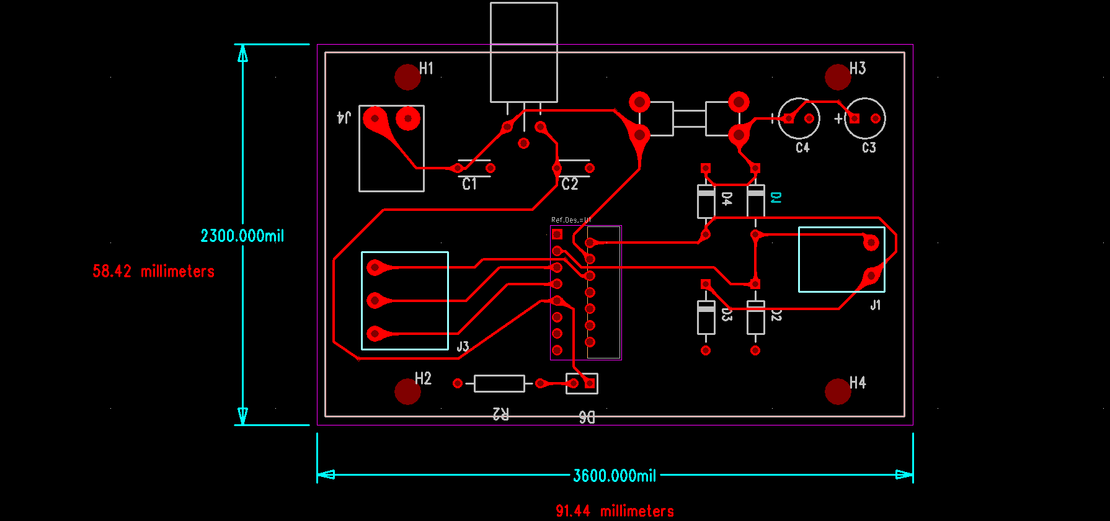
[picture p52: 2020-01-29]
PCB/Layout Prints/hbridge_circuit_pcb.png

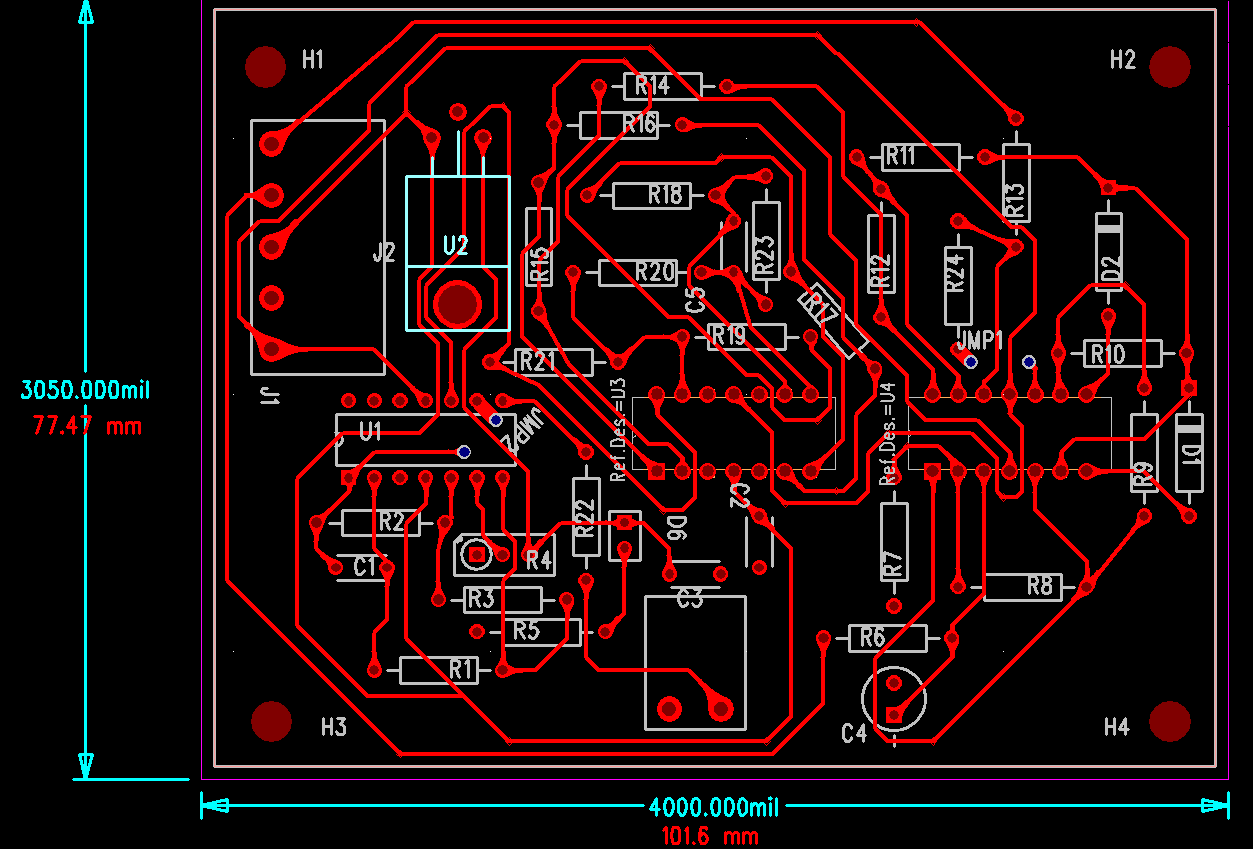
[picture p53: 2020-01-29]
PCB/Layout Prints/pwm_control_pcb.png

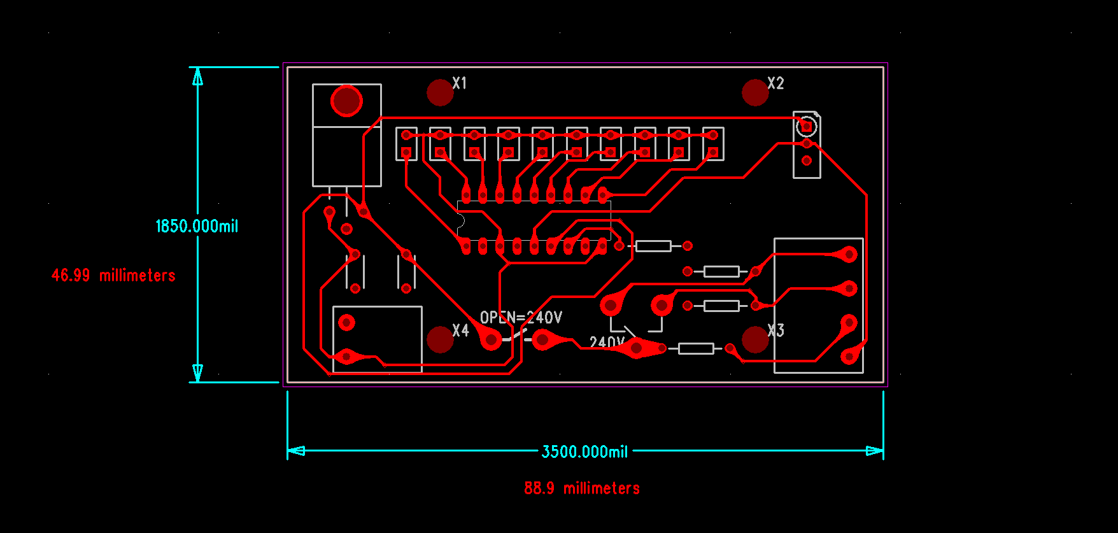
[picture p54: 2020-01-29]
PCB/Layout Prints/hmi_circuit_pcb.png

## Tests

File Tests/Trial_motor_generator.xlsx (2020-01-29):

Ensaio motor-gerador DC
Vmotor [V] | Vgerador [V] | Equação
0 | 0 | -0.5
0.5 | 0 | -0.5
1 | 0.00600 | -0.497
1.5 | 0.011 | -0.4945
2 | 0.016 | -0.492
2.5 | 0.019 | -0.4905
3 | 0.023 | -0.4885
3.5 | 0.028 | -0.486
4 | 0.032 | -0.484
4.5 | 0.037 | -0.4815
5 | 0.042 | -0.479
5.5 | 0.046 | -0.477
6 | 0.049 | -0.4755
6.5 | 0.056 | -0.472
7 | 0.059 | -0.4705
7.5 | 0.063 | -0.4685
8 | 0.069 | -0.4655
8.5 | 0.072 | -0.464
9 | 0.076 | -0.462
9.5 | 0.082 | -0.459
10 | 0.085 | -0.4575
10.5 | 0.089 | -0.4555
11 | 0.097 | -0.4515
11.5 | 0.1 | -0.45
12 | 0.103 | -0.4485

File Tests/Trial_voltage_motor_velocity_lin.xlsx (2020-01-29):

Tensão motor/V | delta t1/s | delta t2/s | Média | Velocidade/(m/s)
0 | Não arranca | Não arranca | ********* | 0
1 | Não arranca | Não arranca | ********* | 0
2 | 6.5 | 6.6 | 6.55 | 0.03053435115
3 | 3.7 | 3.6 | 3.65 | 0.05479452055
4 | 2.7 | 2.6 | 2.65 | 0.07547169811
5 | 2 | 2 | 2 | 0.1
6 | 1.7 | 1.7 | 1.7 | 0.1176470588
7 | 1.5 | 1.3 | 1.4 | 0.1428571429
8 | 1.2 | 1.2 | 1.2 | 0.1666666667
9 | 1 | 1.1 | 1.05 | 0.1904761905
10 | 0.9 | 1 | 0.95 | 0.2105263158
11 | 0.8 | 0.9 | 0.85 | 0.2352941176
12 | 0.7 | 0.8 | 0.75 | 0.2666666667
delta x /m
0.2
